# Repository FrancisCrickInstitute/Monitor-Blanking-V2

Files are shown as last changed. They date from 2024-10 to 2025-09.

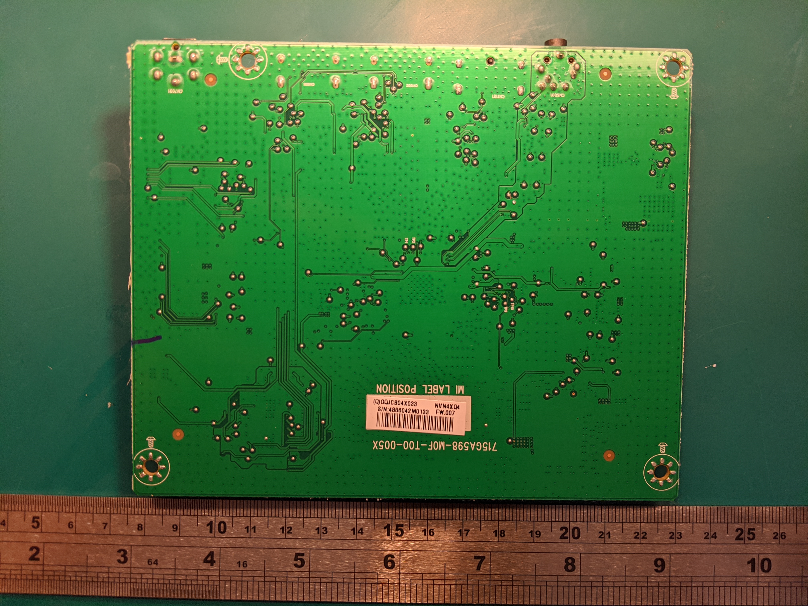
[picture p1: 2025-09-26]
monitor blanking/monitor blanking/IMG_20200924_165727.jpg

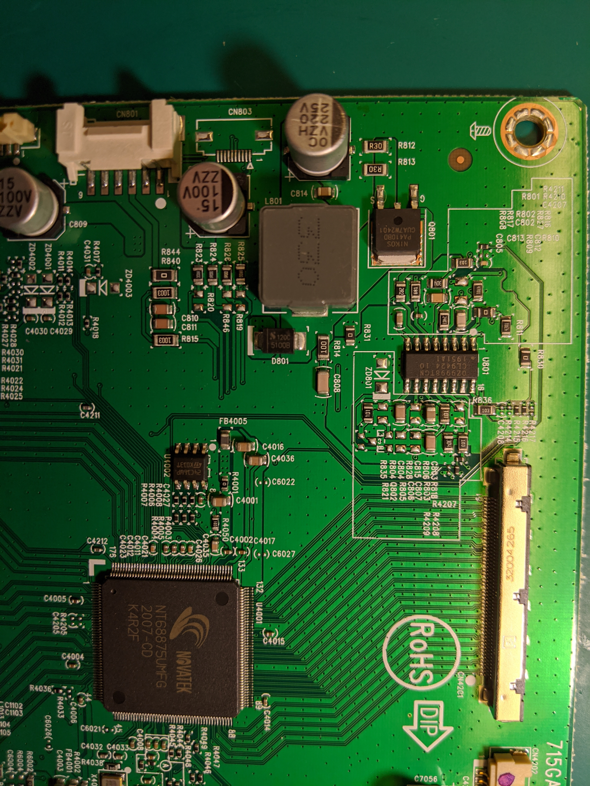
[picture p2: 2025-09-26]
monitor blanking/monitor blanking/IMG_20200924_170019.jpg

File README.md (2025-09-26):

# Bill of materials

1) 1 x 3D printed case
2) 1 x 3D printed base
3) 1 x [Driver board](https://github.com/FrancisCrickInstitute/Monitor-Blanking-V2/tree/main/Driver%20PCB)
4) 1 x [Boost converter](https://www.amazon.co.uk/gp/product/B0897K55JD/ref=ppx_yo_dt_b_asin_title_o09_s00?ie=UTF8&psc=1)
5) 2 x M3 nuts
6) 2 x M3 screws 12-16 mm length
7) 2 x Self tapping screws
8) 1 x [Barrel jack connector (panel mount)](https://www.amazon.co.uk/gp/product/B00WZ7UX6C/ref=ppx_yo_dt_b_asin_title_o01_s00?ie=UTF8&psc=1)
9) 1 x [Barrel jack connector Y splitter](https://www.amazon.co.uk/gp/product/B0C9TR26LD/ref=ppx_yo_dt_b_asin_title_o08_s00?ie=UTF8&psc=1)

# Assembly instructions

### 1. Download the STL files and 3D print the case
### 2. Order the materials from the bill of materials including driver boards manufacturing and assembly on [JLCPCB](https://jlcpcb.com/)
### 3. Open the back cover of the display (Careful when opening the back cover, there is a small joistick connector between the back cover and the front that keep both together!!)
   
### 4. Unplug the Joistick connector
   
### 5. Unplug the Backlight connector
   
### 6. Use the 3D printed base as a template to drill the holes on the back cover (3mm drillbit)
   
### 7. Drill the hole for the backlight connector (12mm drillbit)
   
### 8. Glue M3 nuts on the base holes
   
### 9. Use M3 screws to attach the base with the back cover
   
### 10. Place the boost converter and the driver board on the base (they slide in inside the rails only in one direction until they reach a stop)
   
   

### 11. Solder the barrel jack connector into the input pins of the boost converter( We recommend cheching the polarity of the positive (internal pin) and negative pins and cut away the 3rd (sleeve) pin 
   

### 12. Adjust the voltage of the boost converter by connecting the barrel jack to the display power supply and the output to the multimiter terminals, then use a small flat screwdriver to adjust the output voltage to 54V
   
   
### 13. Solder the boost output wires to the +(red) and -(black) terminals of the driver board
   

### 14. Put the top cover of the box inserting first the barrel jack connector through the hole and hold it in place using the nut.

### 15. Connect the backlight connector through the hole on the box


### 16. Insert the two self threading screws on the box sides to keep the top in place


### 17. Connect back the joistick connector


### 18. Close the back cover

### 19. Put the switch in the wanted position (inverted/non inverting)

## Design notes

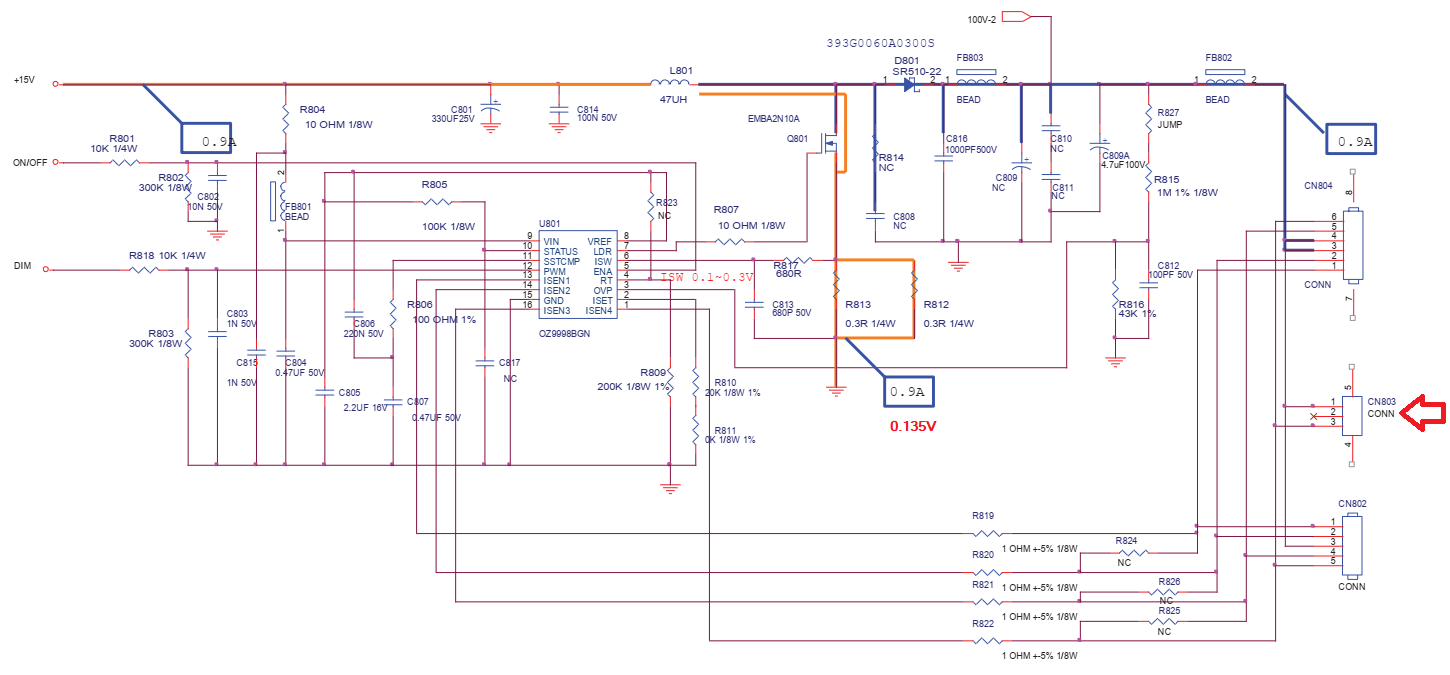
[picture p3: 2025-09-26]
monitor blanking/monitor blanking/671360254_OZ9998U801AOCe970SWNL.png.de07fccf83c527b98e20021ee3e848f6.png

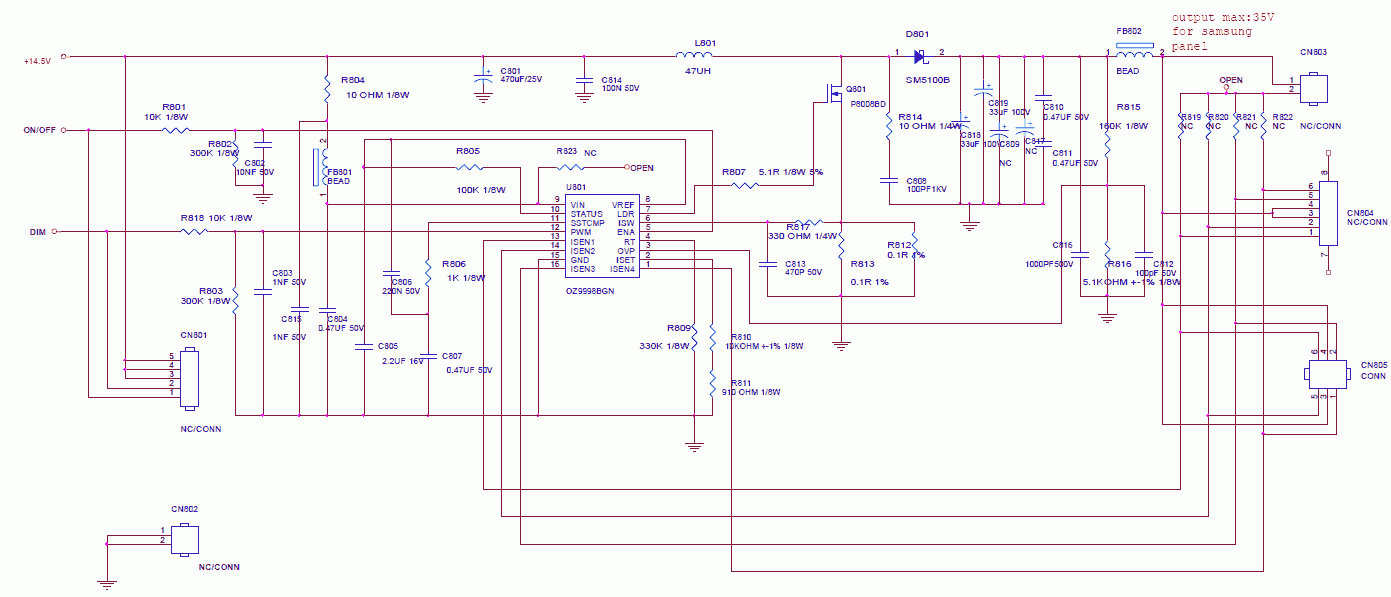
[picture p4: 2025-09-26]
monitor blanking/monitor blanking/b89882ddeaf6fee388e2dc93e1b46374.gif

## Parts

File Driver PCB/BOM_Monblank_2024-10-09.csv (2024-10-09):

ID | Name | Designator | Footprint | Quantity | Manufacturer Part | Manufacturer | Supplier | Supplier Part | Price | Pins
1 | 2.4kΩ | R5 | R2010 | 1 | RS-10K242JT | FH(风华) | LCSC | C341639 | 0.012 | 2
2 | BX-HY2.0-6PWT | BACKLIGHT,MOTHERBOARD | CONN-SMD_6P-P2.0_BX-HY2.0-6PWT | 2 | BX-HY2.0-6PWT | Bossie(博锡) | LCSC | C18077775 | 0.097 | 8
3 | BZV55B24 | D1 | SOD-80_L3.5-W1.5-RD | 1 | BZV55B24 | LGE(鲁光) | LCSC | C545336 | 0.012 | 2
4 | 12Ω | R1,R2,R3,R4 | R0603 | 4 | AR03BTCX0120 | Viking(光颉) | LCSC | C317931 | 0.031 | 2
5 | MST22D18G2 125 | SW1 | SW-SMD_MST22D18G2 | 1 | MST22D18G2 125 | SHOU HAN(首韩) | LCSC | C2906280 | 0.059 | 6
6 | COS4428SR-SOP8 | U1 | SOP-8_L4.9-W3.9-P1.27-LS6.0-BL | 1 | COS4428SR | COSINE(科山芯创) | LCSC | C2685359 | 0.436 | 8
7 | - | U2,U3,U4,U5 | SOT-26_L3.0-W1.6-P0.95-LS2.8-BL | 4 | BCR420UW6-7 | DIODES(美台) | LCSC | C194381 | 0.136 | 6
8 | 8.2uF | C1,C2 | CAP-SMD_BD8.0-L8.3-W8.3-FD | 2 | VKMD1002D8R2MV | Ymin(永铭) | LCSC | C487493 | 0.104 | 2
9 | 2.2uF | C4,C6 | C1210 | 2 | GRM32ER72A225KA35L | muRata(村田) | LCSC | C86054 | 0.138 | 2
10 | POWER SOLDERING PAD | U6 | POWER SOLDERING PAD (2 PADS) | 1 |  | Pololu | GoTronic |  |  | 2
11 | DOSIN-801-0057 | RF1 | ANT-TH_DOSIN-801-0057 | 1 | DOSIN-801-0057 | dosinconn(德索五金) | LCSC | C709675 | 1.531 | 5

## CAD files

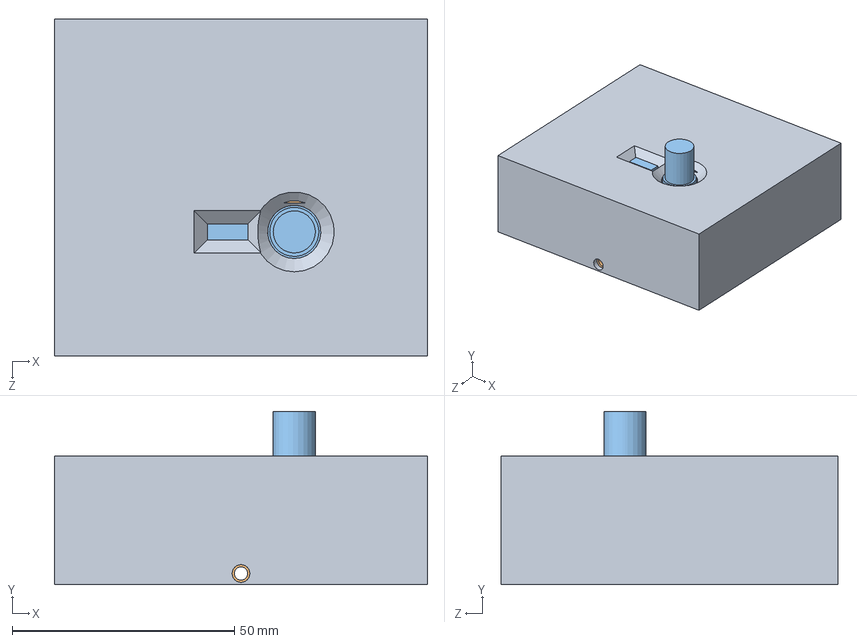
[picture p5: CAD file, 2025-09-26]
monitor blanking/monitor blanking/Assem1.SLDASM
84.0 x 39.0 x 76.0 mm
booster
new_board
case_c
Cover

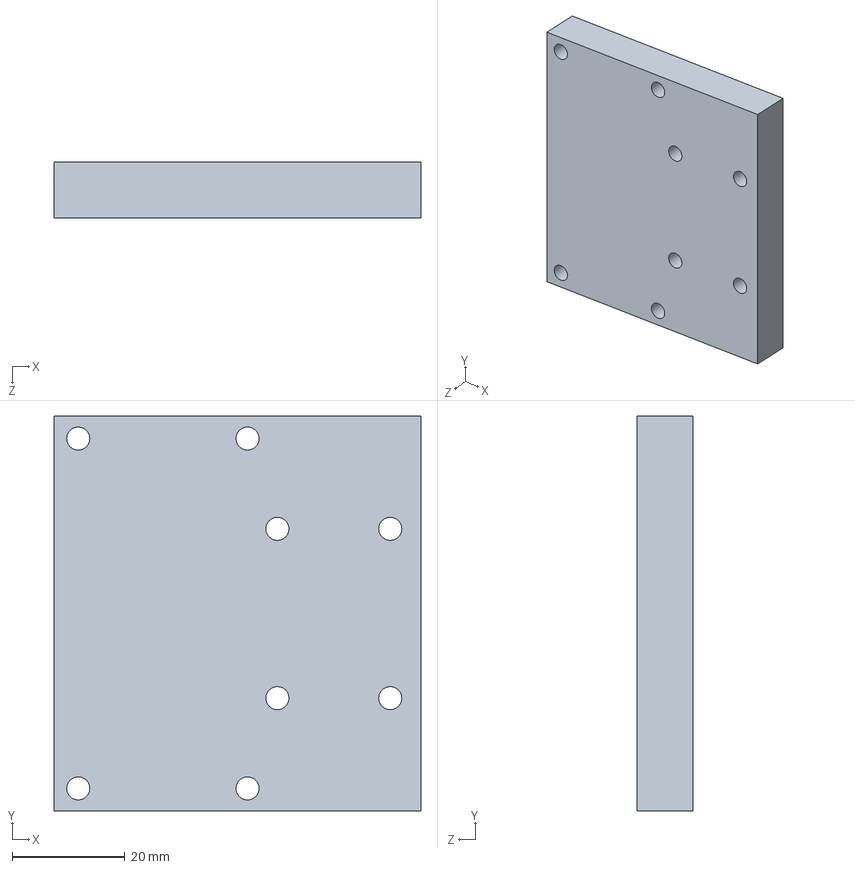
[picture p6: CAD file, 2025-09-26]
Housing/board_holder.SLDPRT
65.0 x 70.0 x 10.0 mm

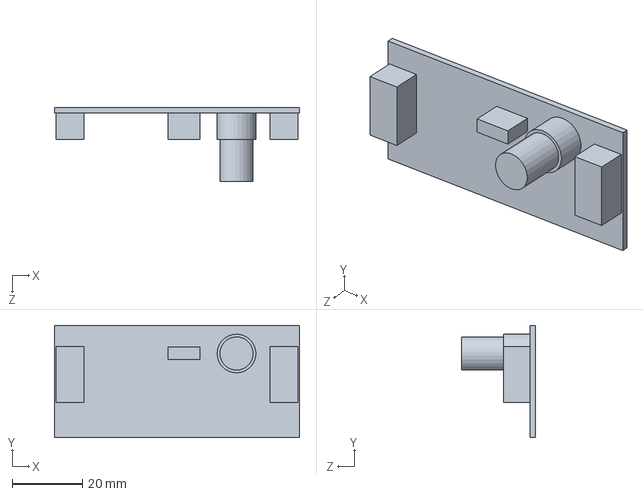
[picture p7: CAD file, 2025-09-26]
Housing/new_board.SLDPRT
70.0 x 32.0 x 21.1 mm

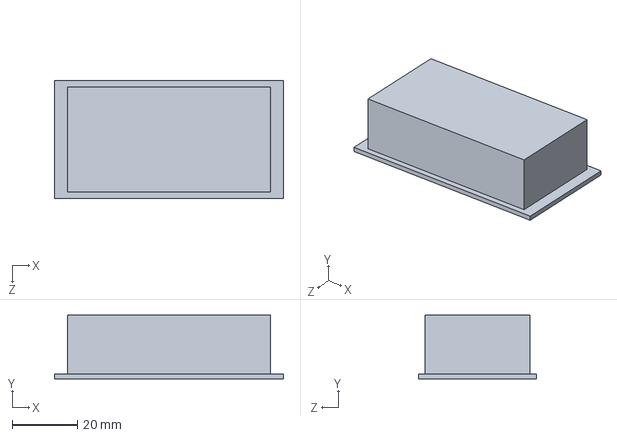
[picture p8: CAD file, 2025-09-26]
monitor blanking/monitor blanking/booster.SLDPRT
70.0 x 19.5 x 36.0 mm

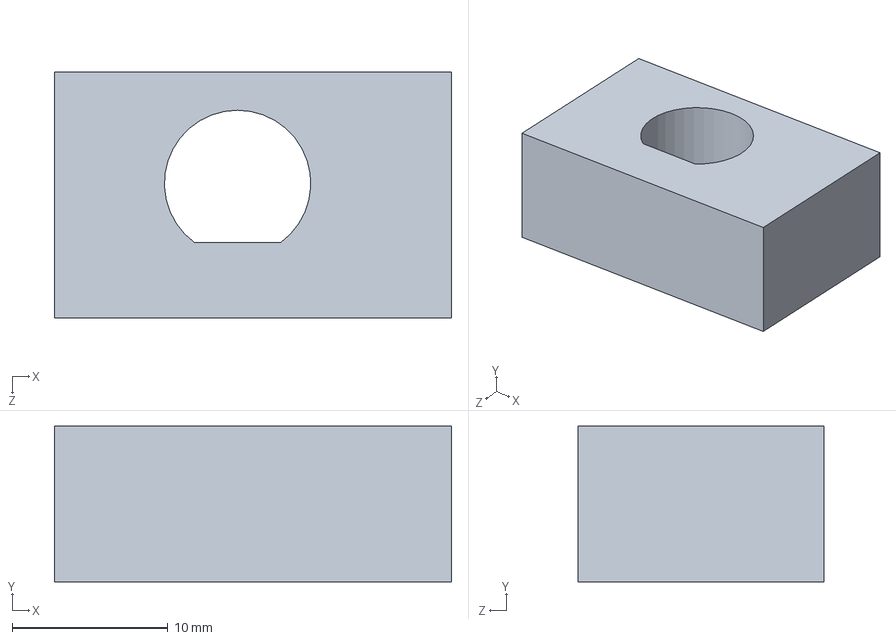
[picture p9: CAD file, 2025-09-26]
Housing/BNC_hole.SLDPRT
25.5 x 10.0 x 15.8 mm

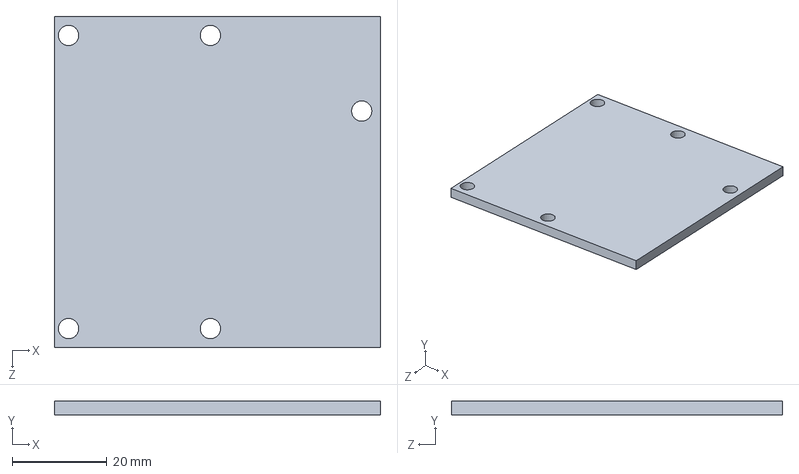
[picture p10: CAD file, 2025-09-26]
Housing/board_holder_2.SLDPRT
69.0 x 3.00 x 70.0 mm

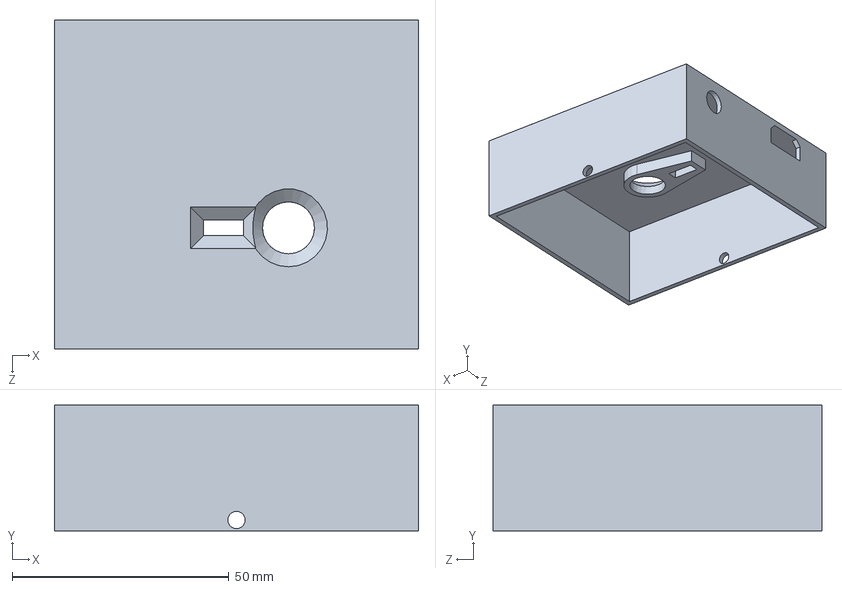
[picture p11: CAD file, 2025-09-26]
Housing/Cover.SLDPRT
84.0 x 29.0 x 76.0 mm

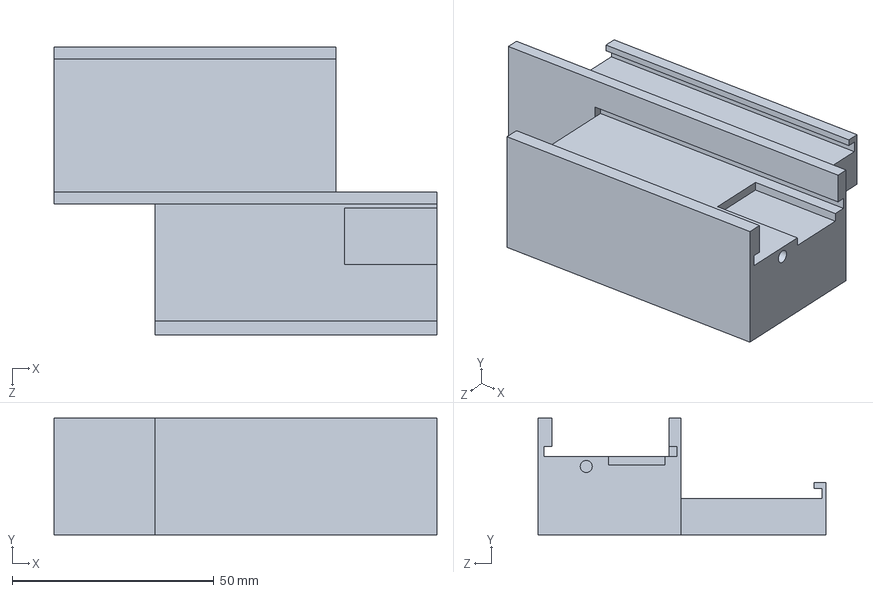
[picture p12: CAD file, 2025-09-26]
Housing/case_b.SLDPRT
95.0 x 29.0 x 71.5 mm

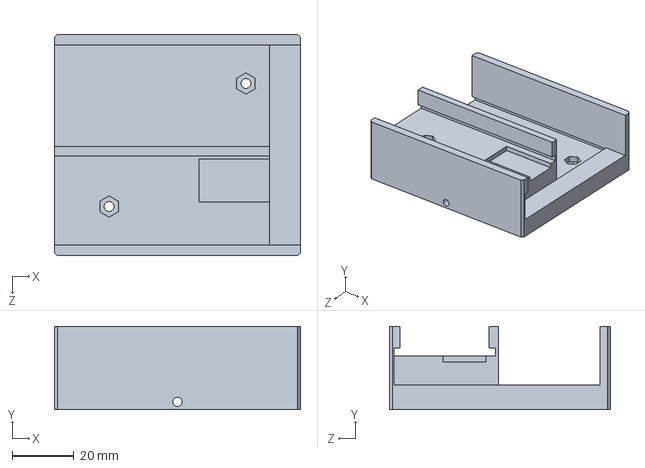
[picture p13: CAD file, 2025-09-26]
monitor blanking/monitor blanking/case_c.SLDPRT
80.0 x 27.0 x 72.0 mm

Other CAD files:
Housing/BNC_hole.DXF
Housing/Cover.STL
Housing/board_holder.DXF
Housing/board_holder_2.DXF
Housing/case_b.STL
Housing/case_c.STL
monitor blanking/monitor blanking/BNC_hole.DXF
monitor blanking/monitor blanking/Cover.STL
monitor blanking/monitor blanking/board_holder.DXF
monitor blanking/monitor blanking/board_holder_2.DXF
monitor blanking/monitor blanking/case_b.STL
monitor blanking/monitor blanking/case_c.STL

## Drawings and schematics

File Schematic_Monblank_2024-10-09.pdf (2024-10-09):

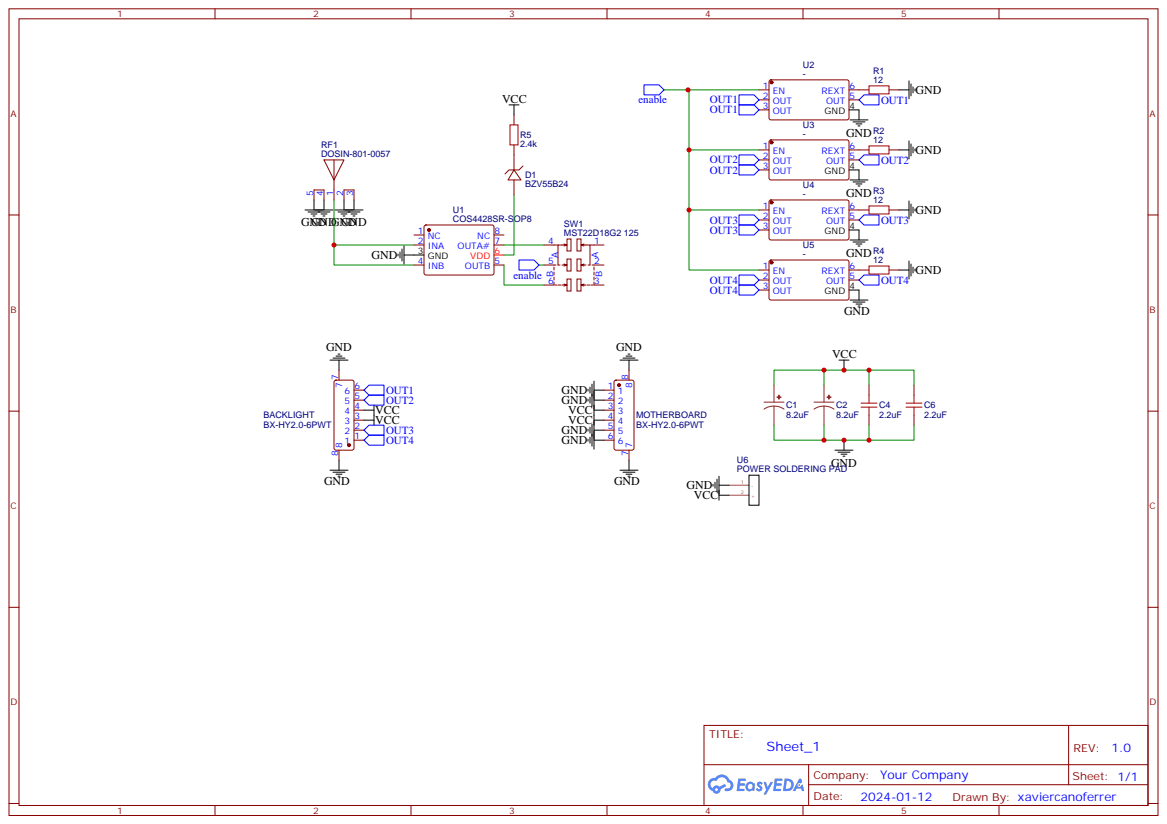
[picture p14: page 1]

GND POWER SOLDERING PAD
